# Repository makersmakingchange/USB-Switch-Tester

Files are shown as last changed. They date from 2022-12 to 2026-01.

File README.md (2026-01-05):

# USB SWITCH TESTER
The USB Switch Tester is used to test the functionality of an assistive switch with a 3.5 mm connection.

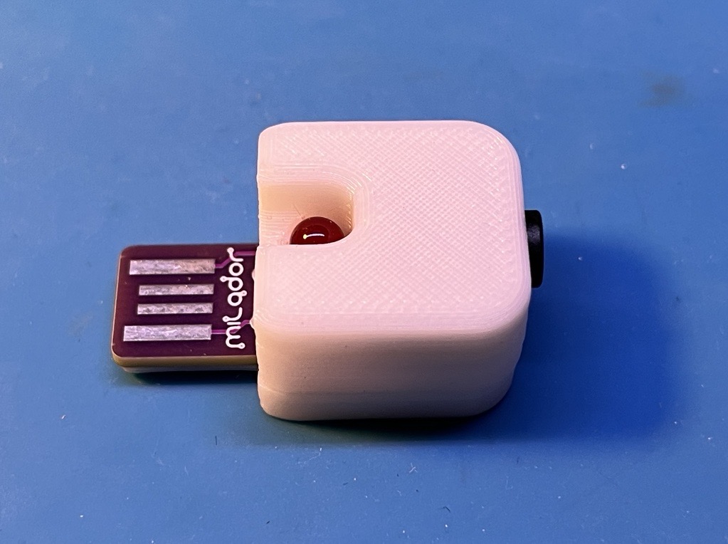
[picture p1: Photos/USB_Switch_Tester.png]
Picture of USB Switch Tester.


## More info at
- [Makers Making Change Assistive Device Library ](https://www.makersmakingchange.com/product/usb-switch-tester/01tJR000000690rYAA)

## How to Obtain a USB Switch Tester
### 1. Do it Yourself (DIY) or Do it Together (DIT)

This is an open-source assistive technology, so anyone is free to build it. All of the files and instructions required to build the USB Swtich Tester are contained within this repository. Refer to the Maker Checklist below.

### 2. Request a build of this device

If you would like to obtain a USB Switch Tester , you may submit a build request through the [MMC Library Page](https://www.makersmakingchange.com/product/usb-switch-tester/01tJR000000690rYAA). The requestor is responsible for the cost of materials and any shipping.

### 3. How to build this device for someone else

If you have the skills and equipment to build this device, and would like to donate your time to create the switch for someone who needs it, visit the [MMC Maker Wanted](https://makersmakingchange.com/maker-wanted/) section.

## Getting Started

### 1. Read the Makers Checklist

The Makers Checklist contains a list of tasks to complete to build the device.

### 2. Order the Off-The-Shelf Components

The [Bill of Materials](/Documentation/USB_Switch_Tester_BOM.xlsx) lists all of the parts and components required to build the USB Switch Tester. The main switch component needs to be ordered online. The rest of the off-the-shelf components are also online or may be available in smaller quantities at your local hardware store or dollar store.

### 3. Print the 3D Printable components

Print the top and bottom components of the case of the device. 

All of the files and individual print files can be in the [/Build_Files/3D_Printing_Files](/Build_Files/3D_Printing_Files/) folder.

### 4. Assemble the USB Switch Tester

Reference the [Assembly Guide](/Documentation/USB_Switch_Tester_Assembly_Guide.pdf) for the tools and steps required to build each portion.

## Files
### Documentation
| Document             | Version | Link |
|----------------------|---------|------|
| Design Rationale     | 1.0     | [USB_Switch_Tester_Design_Rationale](/Documentation/USB_Switch_Tester_Design_Rationale.pdf)     |
| Maker Checklist      | 1.0     | [USB_Switch_Tester_Checklist](/Documentation/USB_Switch_Tester_Maker_Checklist.pdf)     |
| Bill of Materials    | 1.0     | [USB_Switch_Tester_Bill_of_Materials](/Documentation/USB_Switch_Tester_BOM.xlsx)     |
| 3D Printing Guide    | 1.0     | [USB_Switch_Tester_3D_Printing_Guide](/Documentation/USB_Switch_Tester_3D_Printing_Guide.pdf)     |
| Assembly Guide       | 1.0     | [USB_Switch_Tester_Assembly_Guide](/Documentation/USB_Switch_Tester_Assembly_Guide.pdf)     |
| User Guide           | 1.0     | [USB_Switch_Tester_User_Guide](/Documentation/USB_Switch_Tester_User_Guide.pdf)    |
| Changelog            | 1.0     | [USB_Switch_Tester_Changelog](/Documentation/USB_Switch_Tester_Changelog.pdf)     |

### Design Files
 - [CAD Files](/Design_Files/CAD)
 - [PCB Design Files](/Design_Files/PCB)

### Build Files
 - [3D Printing Files](/Build_Files/3D_Printing_Files)
 - [PCB Gerber Files](/Build_Files/PCB_Files)

## Attribution
Designers:
 - Milad Hajihassan
 - Derrick Andrews

## License
Everything needed or used to design, make, test, or prepare the USB Switch Tester is licensed under the CERN 2.0 Weakly Reciprocal license <https://ohwr.org/project/cernohl/wikis/Documents/CERN-OHL-version-2> (CERN-OHL-W) . 

Accompanying material such as instruction manuals, videos, and other copyrightable works that are useful but not necessary to design, make, test, or prepare the USB Switch Tester are published under a Creative Commons Attribution-ShareAlike 4.0 license https://creativecommons.org/licenses/by-sa/4.0/ (CC BY-SA 4.0).

---
<!-- ABOUT MMC START -->

## About Makers Making Change
[Makers Making Change Logo](https://www.makersmakingchange.com/)

Makers Making Change is a program of [Neil Squire](https://www.neilsquire.ca/), a Canadian non-profit that uses technology, knowledge, and passion to empower people with disabilities.

Makers Making Change leverages the capacity of community based Makers, Disability Professionals and Volunteers to develop and deliver affordable Open Source Assistive Technologies.

 - Website: [www.MakersMakingChange.com](https://www.makersmakingchange.com/)
 - GitHub: [makersmakingchange](https://github.com/makersmakingchange)
 - Bluesky: [@makersmakingchange.bsky.social](https://bsky.app/profile/makersmakingchange.bsky.social)
 - Instagram: [@makersmakingchange](https://www.instagram.com/makersmakingchange)
 - Facebook: [makersmakechange](https://www.facebook.com/makersmakechange)
 - LinkedIn: [Neil Squire Society](https://www.linkedin.com/company/neil-squire-society/)
 - Thingiverse: [makersmakingchange](https://www.thingiverse.com/makersmakingchange/about)
 - Printables: [MakersMakingChange](https://www.printables.com/@MakersMakingChange)

### Contact Us
For technical questions, to get involved, or to share your experience we encourage you to [visit our website](https://www.makersmakingchange.com/) or [contact us](https://www.makersmakingchange.com/s/contact).
<!-- ABOUT MMC END -->

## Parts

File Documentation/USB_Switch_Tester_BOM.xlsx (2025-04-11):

USB Switch Tester |  |  |  |  |  |  |  | Unit Cost | Total Cost | Total Print time (hr) | Total filament (g)
Version: V1.0 |  | Last Updated: 2022-11-21 |  |  |  |  |  | $7.74 | $30.05 | 0.45 | 3.78
Commercial Parts
ID | Part Name | Part Type | QTY | QTY/PKG | $/PKG | PKG QTY | $/Unit | Extended | Total | Link
 | Led, 5 MM, Red | Electrical | 1 | 1 | $0.66 | 1 | $0.66 | $0.66 | $0.66 | https://www.mouser.ca/ProductDetail/604-WP7113ID5V
 | Resistor, 1 kOhms, 1/4W, Through Hole | Electrical | 1 | 1 | $0.24 | 1 | $0.24 | $0.24 | $0.24 | https://www.mouser.ca/ProductDetail/KOA-Speer/CFS1-4C102J?qs=9IB2bDhijq9MRkvwLBYZPw%3D%3D
 | Jack, 3.5 mm, Stereo, STX-3120-3B | Electrical | 1 | 1 | $1.15 | 1 | $1.15 | $1.15 | $1.15 | https://www.mouser.ca/ProductDetail/806-STX-3120-3B
3D Printed Parts ESTIMATED PRICING USING 1KG ROLL COST: |  | $25.00
ID | Part | Material | QTY | Mass (g) / Unit | Time / Unit Min |  | Print Time (Min) | Estimated Price |  | Link
 | Bottom | PLA ( 20% Infill ) | 1 | 1.49 | 10 |  | 10 | $0.04
 | Top | PLA (20% Infill ) | 1 | 2.29 | 17 |  | 17 | $0.06
 |  |  |  |  |  |  |  | $0.00
Custom Printed Circuit Board (PCB)
ID | Part |  | QTY
 | USB_Switch_Tester.zip |  | 1 | 5 | $28.00 | 1 | $5.60 | $5.60 | $28.00 | Build_Files/PCB_Files/Gerber_Files/USB_Switch_Tester.zip
Tools for Assembly
Soldering iron
flush cutters
Alternatives (if there are other sources for some parts link them below)
ID | Part and description |  |  |  |  |  |  |  |  | Link

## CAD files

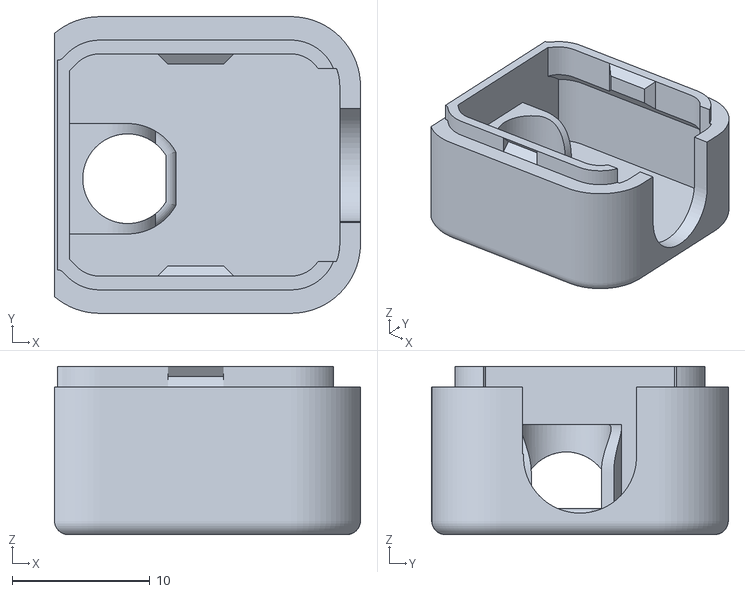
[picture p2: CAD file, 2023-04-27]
Build_Files/3D_Printing_Files/USB_Switch_Tester_Top_Case.stl
22.2 x 21.5 x 12.2

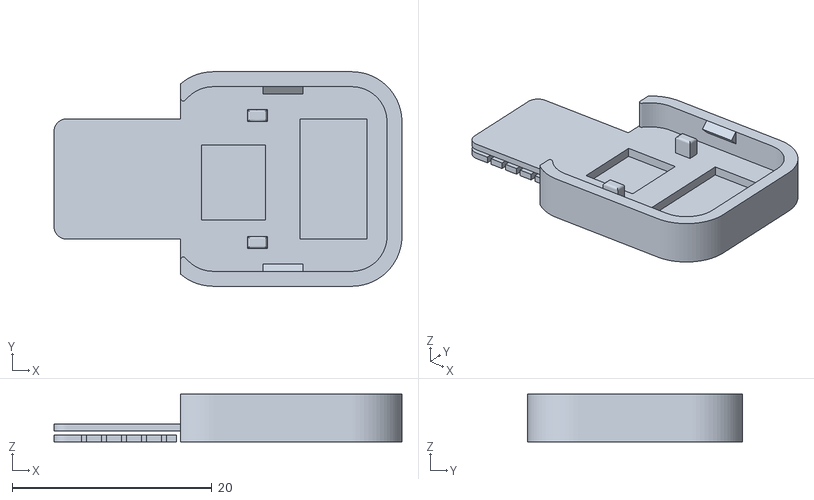
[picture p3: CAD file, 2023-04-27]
Build_Files/3D_Printing_Files/USB_Switch_Tester_Bottom_Case.stl
34.9 x 21.5 x 4.80

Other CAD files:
Design_Files/CAD/STEP/USB_Switch_Tester_Top_Case.step
Design_Files/CAD/STEP/USB_Switch_Tester_Bottom_Case.step
Design_Files/CAD/Fusion/USB_Switch_Tester.f3d
Design_Files/CAD/Fusion/USB_Switch_Tester_Complete.f3z

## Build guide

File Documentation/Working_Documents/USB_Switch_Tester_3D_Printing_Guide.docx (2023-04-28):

# 3D Printing Summary

Metrics
Total Print Time (min) | 30
Total Number of Components | 2
Typical Total Mass (g) | 3.76
Typical Number of Print Setups | 1

# 3D Printing Settings

Print File Name | Qty | Total Print Time (hr:min) | Mass (g) | Infill (%) | Support(Y/N) | Layer Height/ Nozzle Diameter(mm) | Notes (orientation, special settings, etc.)
Bottom_Case.stl | 1 | 0:12 | 1.56 | 20 | N | 0.2/0.4 | Print in default orientation shown below.
Top_Case.stl | 1 | 0:18 | 2.20 | 20 | N | 0.2/0.4 | Print in default orientation shown below.

## Default Orientation

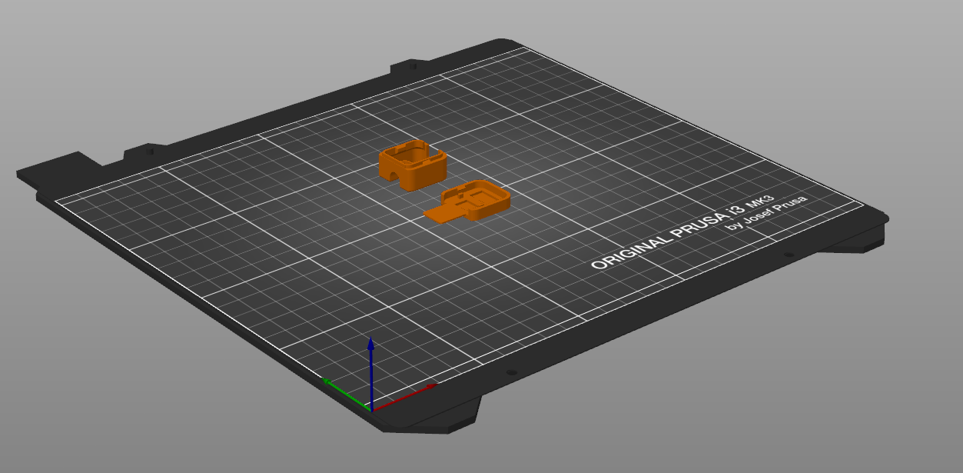
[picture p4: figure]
Photo of the top and bottom case inside of the Prusa Slicer software in default orientation.

# Examples of Quality Prints

The below photos are examples of the 3D printed components that are determined to meet the quality necessary for the device to function.

Photos of Top Case

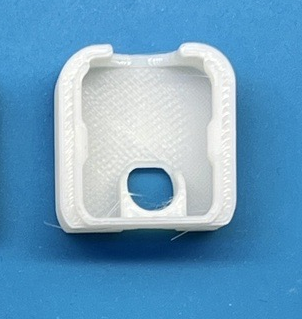
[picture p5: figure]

Photos of Bottom Case

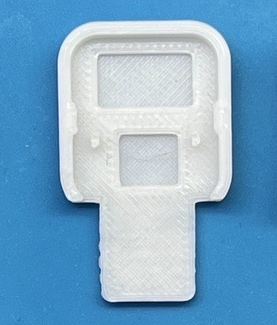
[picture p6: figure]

Photos of Assembly

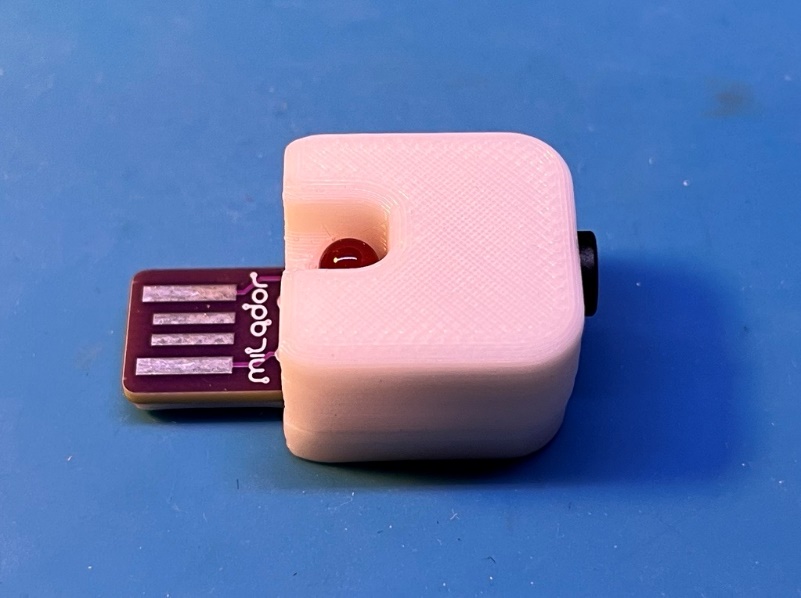
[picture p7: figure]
Photo of assembled top and bottom case with good quality print

© 2022 by Neil Squire / Makers Making Change. This work is licensed under the CC BY SA 4.0 License: http://creativecommons.org/licenses/by-sa/4.0 Files available at https://makersmakingchange.com/project/usb-switch-tester/ Page 1 of 2

V1.0 | April 2023 USB-Switch-Tester 3D Printing Guide

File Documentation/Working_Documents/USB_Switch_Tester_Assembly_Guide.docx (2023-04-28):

# Required Components

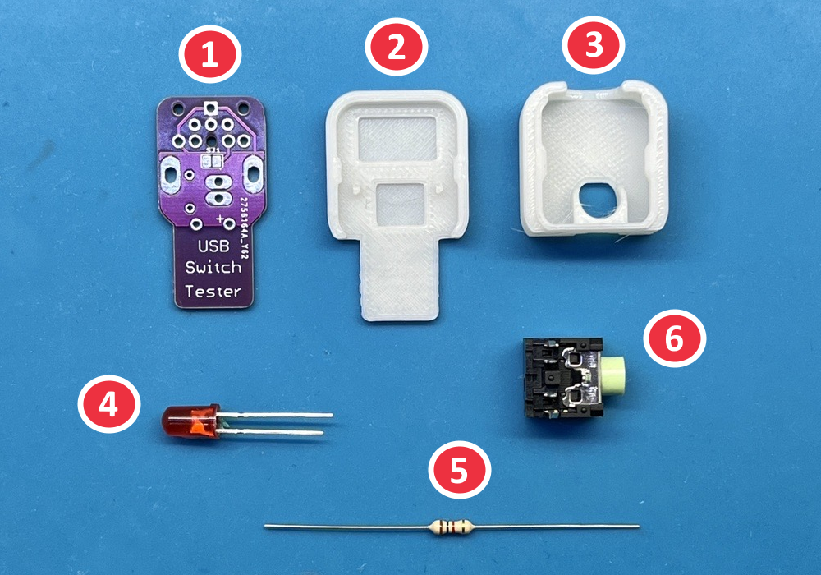
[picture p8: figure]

BOM

1. 1X USB-Switch-Tester PCB (Printed Circuit Board)
2. 1X USB-Switch-Tester Bottom Case
3. 1X USB-Switch-Tester Top Case
4. 1X 5MM Red LED
5. 1X 1KOhm Through-Hole Resistor
6. 1X STX-3120-5B 3.5mm Jack Stereo

# Required Tools

- Temperature regulated soldering Iron
- Phillips Screwdriver
- Side cutters

# Required Personal Protective Equipment (PPE)

- Safety glasses
- Disposable examination gloves (Optional- solder residue may irritate sensitive skin)

# Assembly Instructions

PCB Sides:

In these instructions the terms component side and solder side are used often and are defined below:

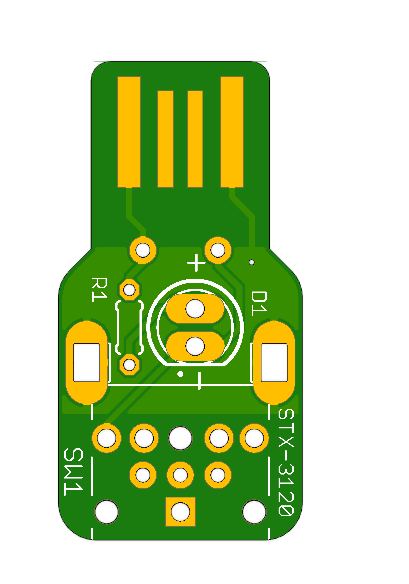
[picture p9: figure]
Component side CAD model of PCB.
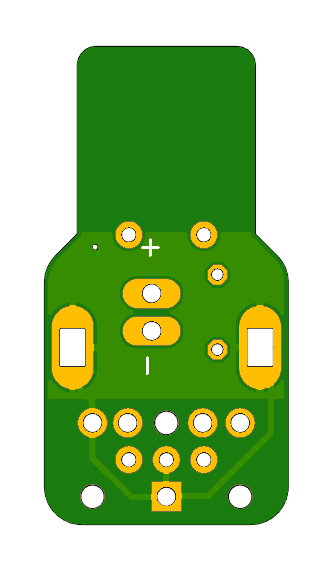
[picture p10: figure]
Solder side CAD model of PCB.

Component Side - USB metal rectangle contact points can be seen. - Visible painted white lines can be seen on this side of the board outlining a circle, R1, and D1. - The side of the PCB board with the label “Milador” is the component side of the PCB (not pictured in above photo). | Solder Side - No USB metal rectangle contact points can be seen - The side of the PCB board with the label “USB Switch Tester” is the component side of the PCB (not pictured in above photo).

## Step 1

Insert the LED into component side of the PCB (shown). Make sure the longer lead of the LED (positive lead) goes into the side marked “+” (closest to USB edge connector). Also ensure the LED is all the way in, and flush with the PCB.

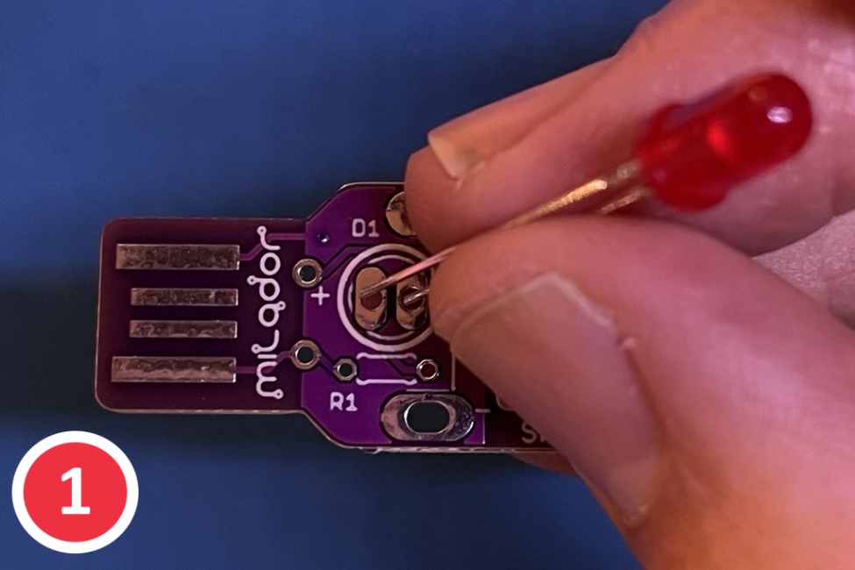
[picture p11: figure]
Component side of PCB facing up with a hand placing in a red LED

## Step 2

Using the heated soldering iron, solder the two LED terminals on the solder side of the PCB.

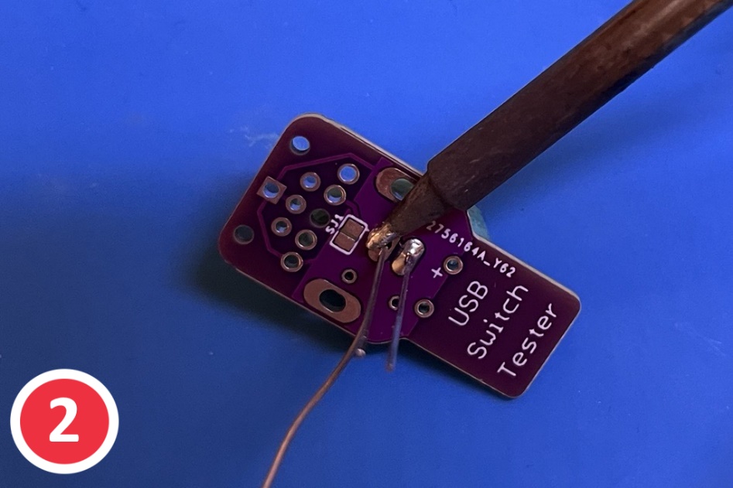
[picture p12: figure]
Soldering the red LED in on the solder side of the PCB

## Step 3

Using side cutters, trim the LED leads from the freshly soldered joints, as close to the board as possible.

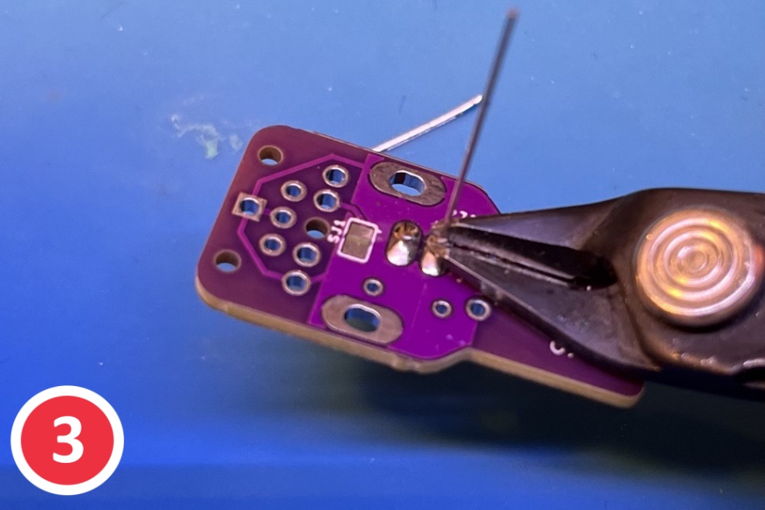
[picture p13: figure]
flush cutters cutting the extra length of the LED leads on the solder side of the PCB

## Step 4

Bend both leads of the 1K resistor (marked with stripes: brown black red) to 90 degrees next to the resistor body. After bending, both resistor leads should be parallel, and pointing in the same direction.

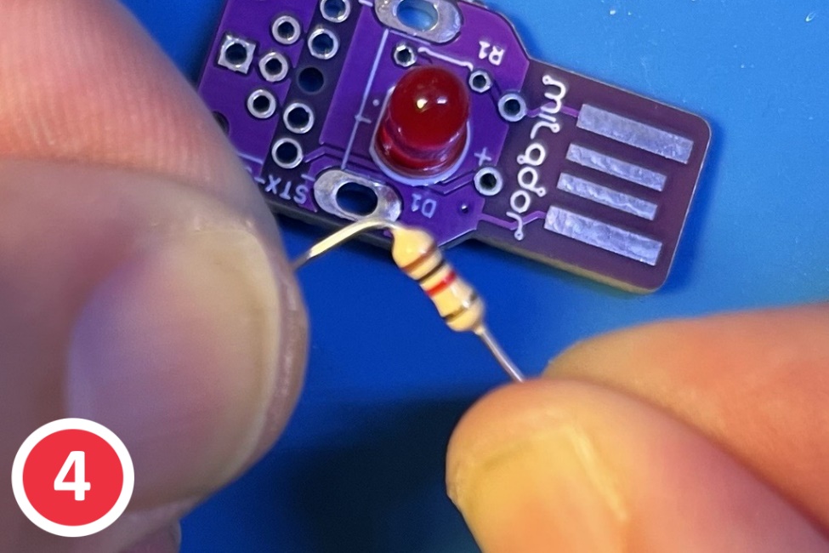
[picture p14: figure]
A hand bending the leads of the resister at 90 degrees

## Step 5

Insert the resistor into the resistor outline R1 holes next to the LED, as shown.

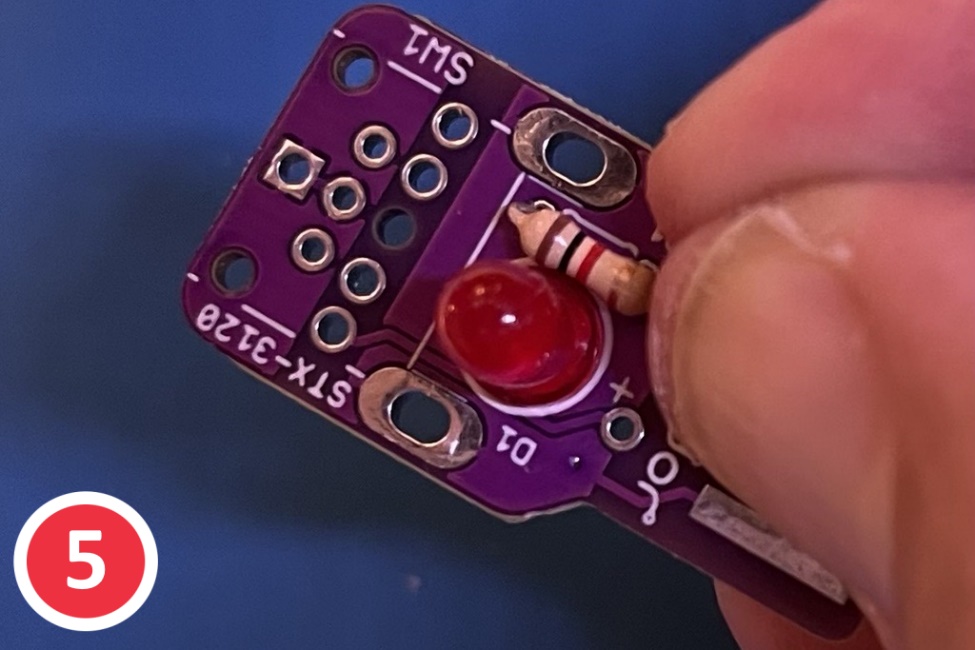
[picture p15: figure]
A hand placing the resistor into the PCB

## Step 6

Ensure the resistor is flush with board, then bend the resistor wires apart slightly, to minimize unwanted part movement during soldering.

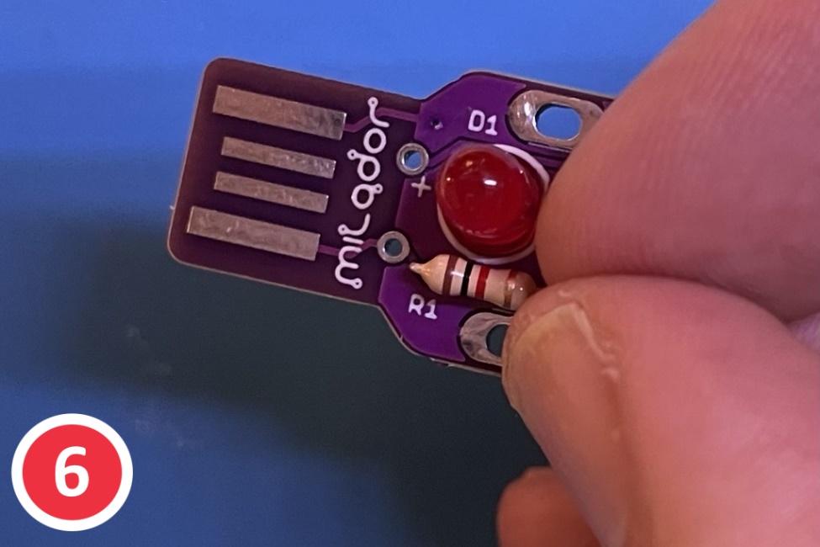
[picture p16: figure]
A finger holding the resistor close to the PCB

## Step 7

Using the heated soldering iron, solder the resistor wires on the solder side of the PCB.

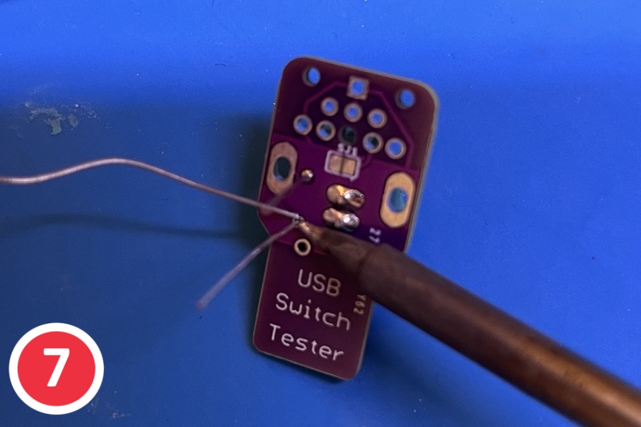
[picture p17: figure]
Soldering the leads of the resistor

## Step 8

Using side cutters, trim the resistor leads from the freshly soldered joints, as close to the board as possible.

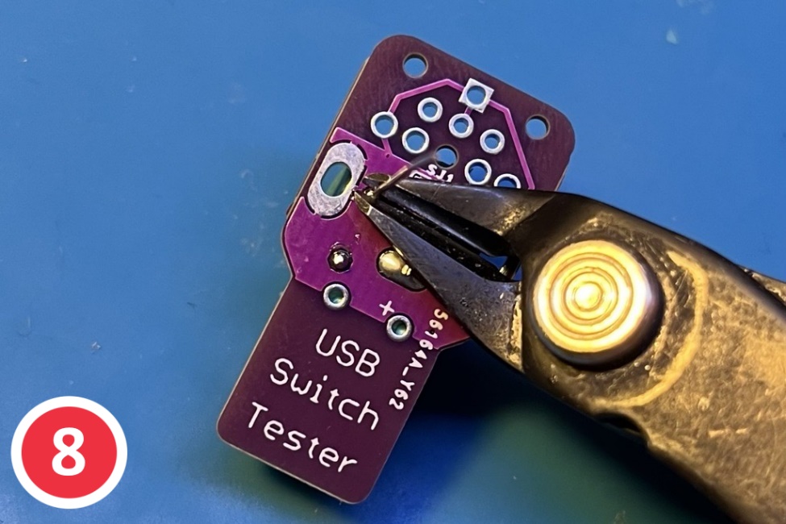
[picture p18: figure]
Using flush cutters to cut the extra of the resistor leads

## Step 9

Insert the 3.5 mm jack pins into the holes on the contact side of the PCB with the jack hole facing away from the LED.

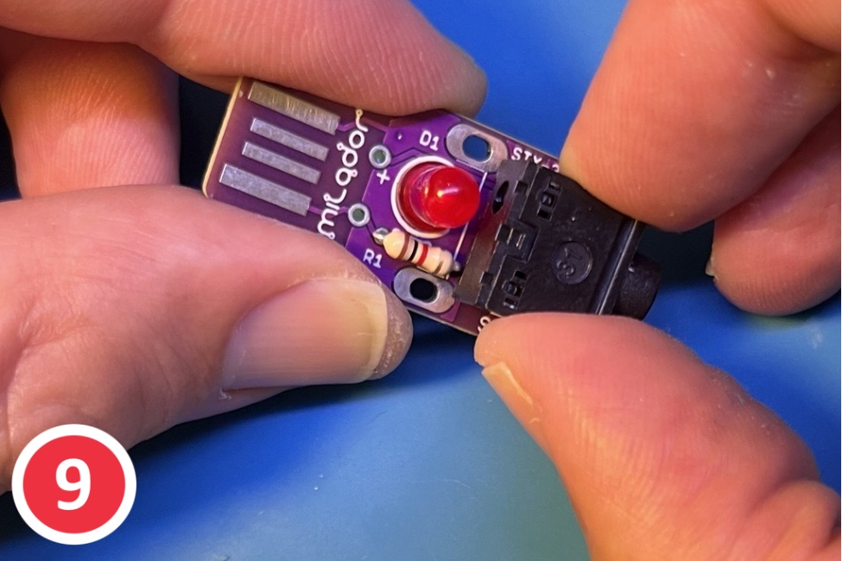
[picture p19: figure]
A hand placing the jack onto the PCB
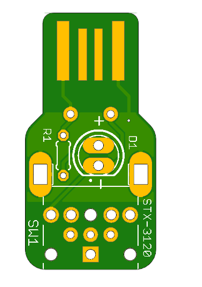
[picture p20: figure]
Photo of CAD model of PCB with a red arrow pointing to the holes the jack will fit into

## Step 10

Using the heated soldering iron, solder the 3.5 mm jack pins on the solder side of the PCB.

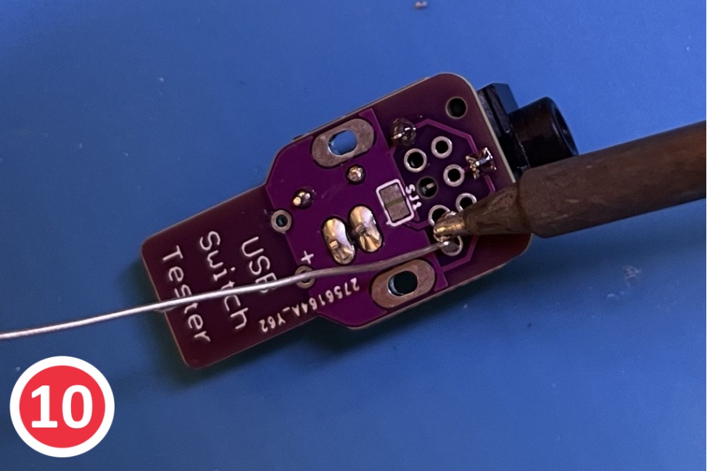
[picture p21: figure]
Soldering the leads of the jack

## Step 11

Using side cutters, trim the 3.5 mm jack leads from the freshly soldered joints, as close to the board as possible.

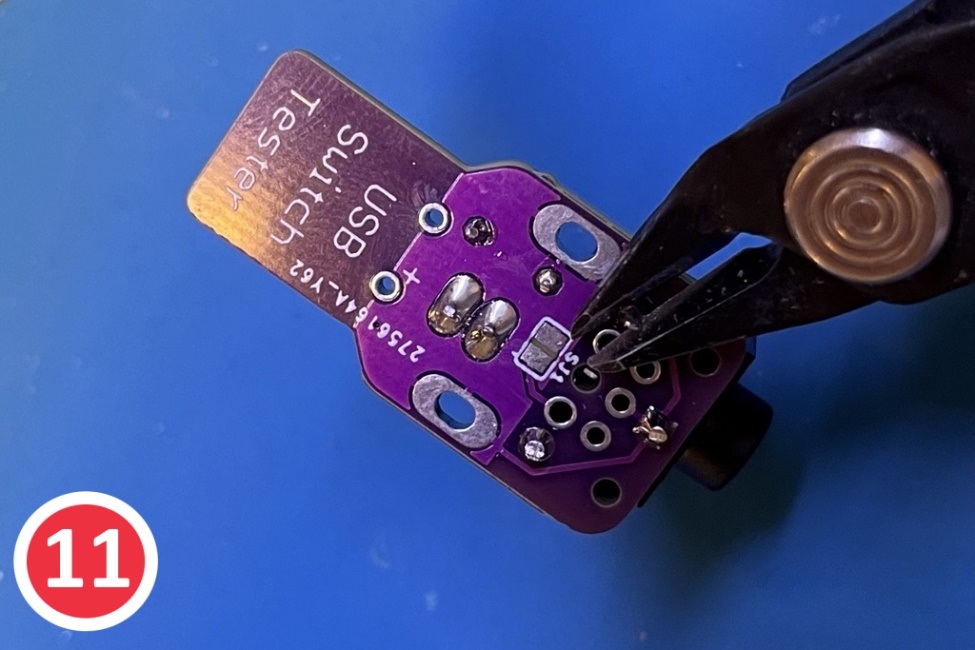
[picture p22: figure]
using flush cutters to cut the extra on the leads of the jack

## Step 12 – Preliminary Testing

All electronic components are now assembled and the device can be tested. To test follow the steps below:

1. Plug in the PCB into a USB port that has power. An example of this would be to plug the USB into a USB Type A port on a laptop.
2. Plug in an adaptive switch with a 3.5 mm plug into the 3.5 mm jack.
3. Press down on the adaptive switch
4. If the light:
  a. Turns on when you press the adaptive switch the test was successful and move on to Step 13.
  b. Does not turn on check the solder connections on the solder side of the device and make sure there is no connections touching.

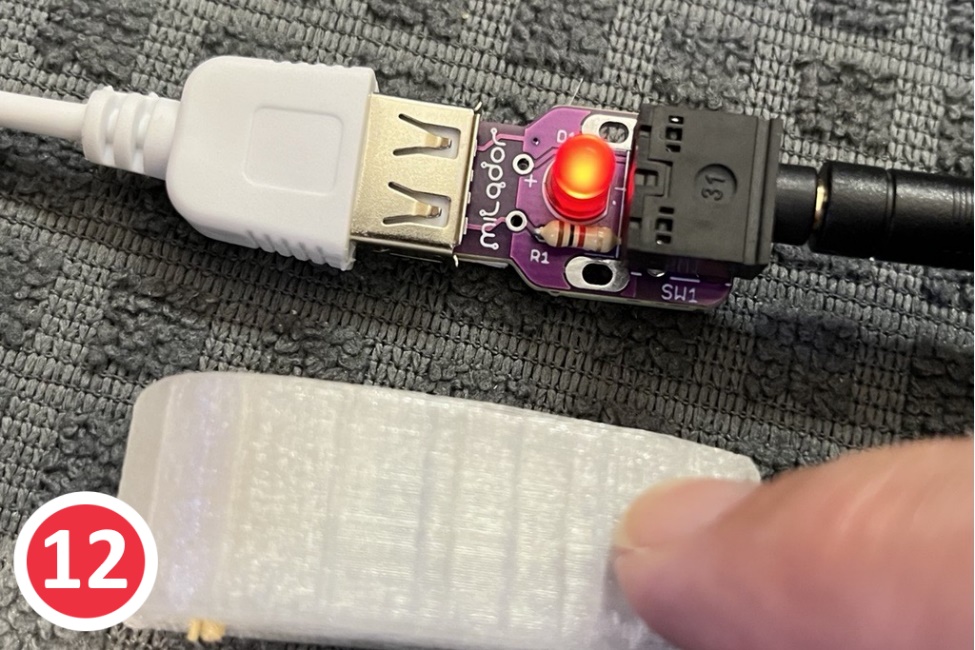
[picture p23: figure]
Photo of the USB switch tester plugged into a USB port and a finger pressing an assistive switch that is plugged into he USB Switch Tester. The red LED light is turned on.

## Step 13

Insert the electronic assembly into the 3D printed top case. Locate the cut outs on the top case for the 3.5 mm jack and LED. Ensure the jack and LED fit inside of these exits.

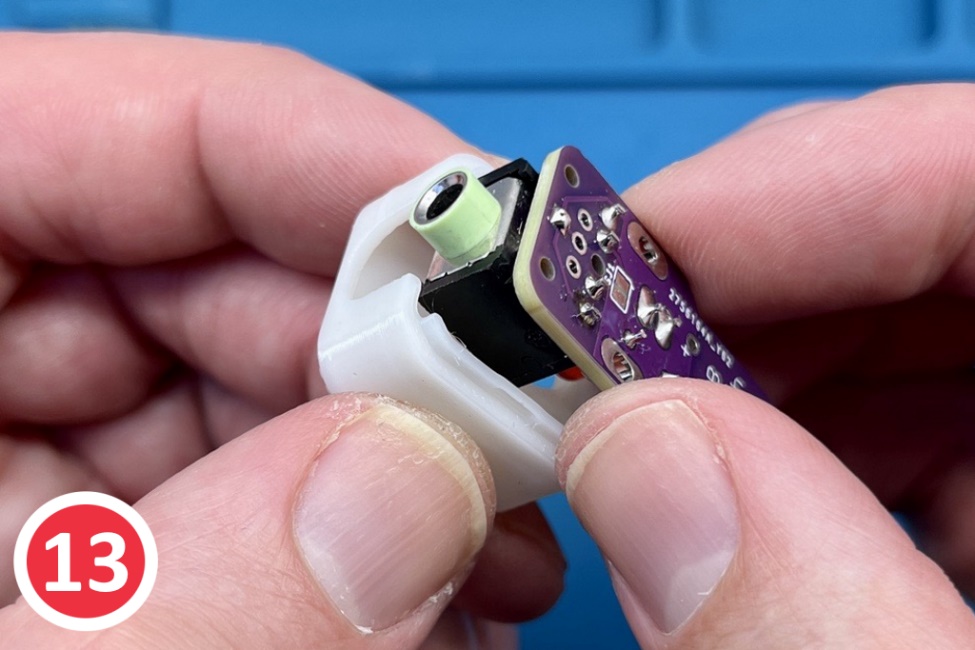
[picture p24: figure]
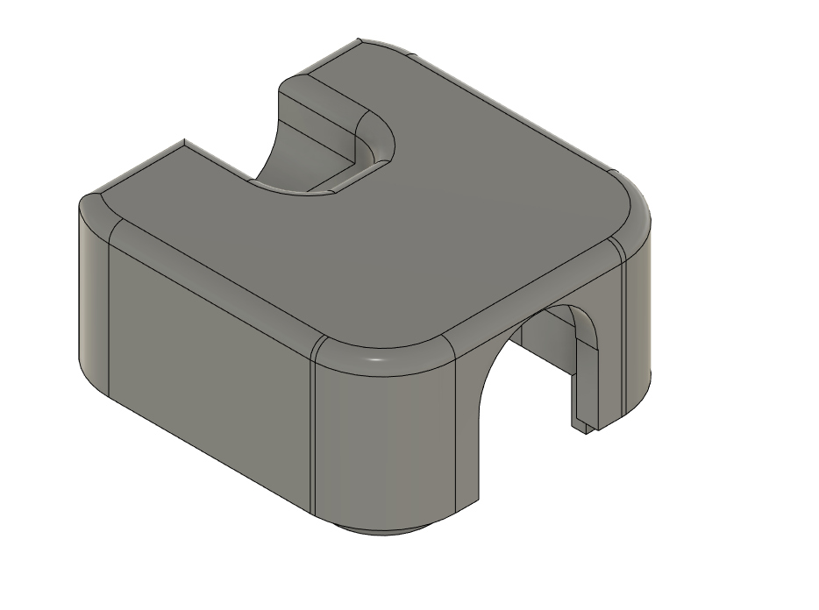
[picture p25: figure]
A photo with a red arrow pointing to the jack exit
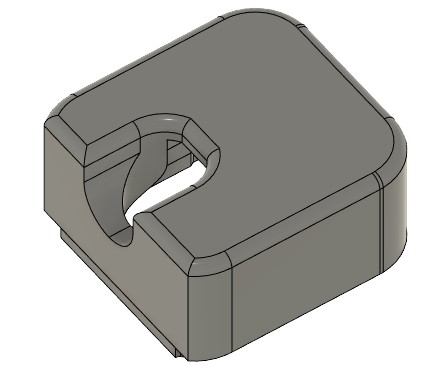
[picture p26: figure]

| 3.5 mm Jack exit LED exit

## Step 14

Place the 3D printed bottom case on the solder side of the PCB and press down gently until you feel the top and bottom case clip together. After the top and bottom case are clipped together the whole device should feel secured.

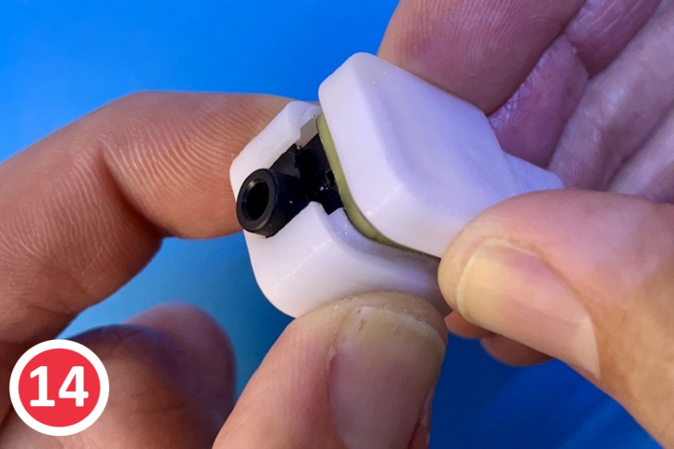
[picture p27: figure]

## Step 15

The assembly is complete, congratulations! Please refer to the Maker Checklist document that can be found on the website page for this device for the next steps.

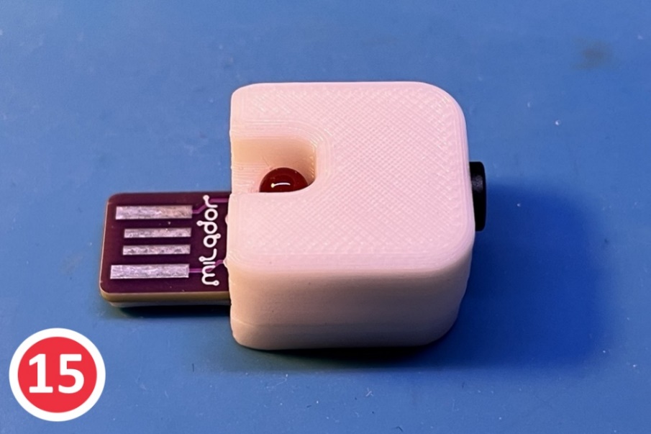
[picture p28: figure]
A photo of the assembled USB Switch Tester device

© 2022 by Neil Squire / Makers Making Change. This work is licensed under the CC BY SA 4.0 License: http://creativecommons.org/licenses/by-sa/4.0 Files available at https://makersmakingchange.com/project/usb-switch-tester/ Page 1 of 1

V1.0 | April 2023 USB-Switch-Tester Assembly Guide

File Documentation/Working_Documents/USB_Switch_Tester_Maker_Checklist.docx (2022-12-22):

# Maker To Do List

- Read through the Assembly Guide to become familiar with required components, tools, supplies, and safety gear and overall assembly steps.
- Talk to User about customization options (e.g., color, any special requests, etc.)
- Order hardware components
- Gather tools, supplies, and safety equipment.
- Assemble the device
- Test device
- Print “User Quick Guide”

# Items to Give to User

- Assembled, tested device
- “User Quick Guide”

© 2022 by Neil Squire / Makers Making Change. This work is licensed under the CC BY SA 4.0 License: http://creativecommons.org/licenses/by-sa/4.0 Files available at https://makersmakingchange.com/project/usb-switch-tester/ Page 1 of 1

V1.0 | December 2022 USB-Switch-Tester Maker Checklist

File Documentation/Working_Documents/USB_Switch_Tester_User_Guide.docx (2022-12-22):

## Introduction

This USB Switch Tester is a device that allows someone to confirm their assistive switch with a 3.5 mm plug is functional. This convenient device can be plugged into USB Type-A ports with power (for example, a laptop) and assistive switches can be plugged in to the 3.5 mm jack on the USB switch tester. When the assistive switch is pressed down, the LED on the device will light up indicating that the assistive switch is working. If the assistive switch is not working, the LED on the USB Switch Tester will not light up. This device will be helpful to disability professionals or individuals who use assistive switches to check to make sure their devices are in working condition.

This is NOT a switch interface but rather a simple device to confirm your assistive switch is working properly.

## Features

The USB Switch Tester features an LED light, USB plug, 3D printed casing, and a 3.5 mm port as shown in the photo below.

LED light – Lights up when a working assistive switch is pressed.

3.5 mm port – Location where assistive switches with a 3.5 mm plug will be inserted.

USB plug – Allows device to be inserted into a powered USB port.

3D printed casing – hard outer shell that protects the internal electrical components.

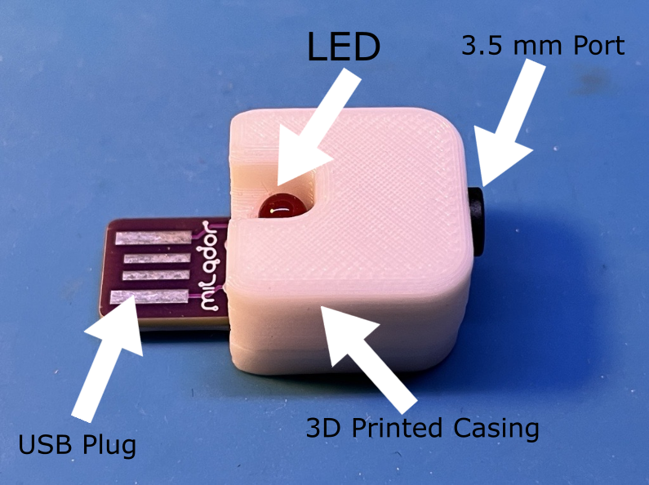
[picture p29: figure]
A photo of the assembled USB Switch testers with white arrows pointing to the LED, 3.5 mm port, 3D printed casing, and USB plug

## Usage

This device requires a USB port that has power coming from it and an assistive switch to test. The setup should look similar to the one shown in the photo below. With these materials, follow the below steps:

1. Plug the USB Switch Tester into the powered USB port (see compatibility section to see powered USB ports).
2. Plug in the assistive switch that you would like to test
3. Press down on the assistive switch
  a. If the LED on the USB Switch Tester lights up, the assistive switch is functional
  b. If the LED on the USB Switch Tester does not light up, the assistive switch is not working
4. Unplug the assistive switch from USB Switch Tester and repeat steps above if you want to test another assistive switch

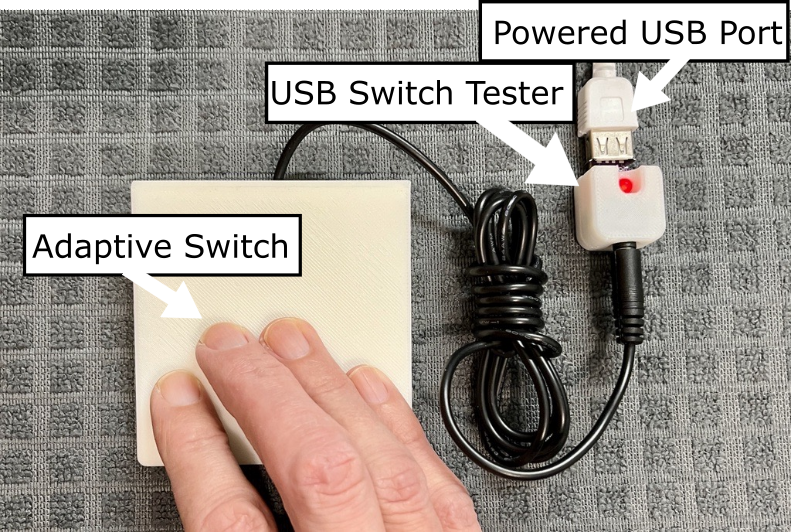
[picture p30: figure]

## Compatibility

This device needs to be plugged into a powered USB source. There are many options for this as the device does not draw more than 20 mA of current from the power source. The USB Switch Tester can be plugged into any power source with USB Type-A port such as laptops, USB block chargers, etc.

In the example photo below, the USB Switch Tester is plugged into a USB block charger that is connected to an outlet.

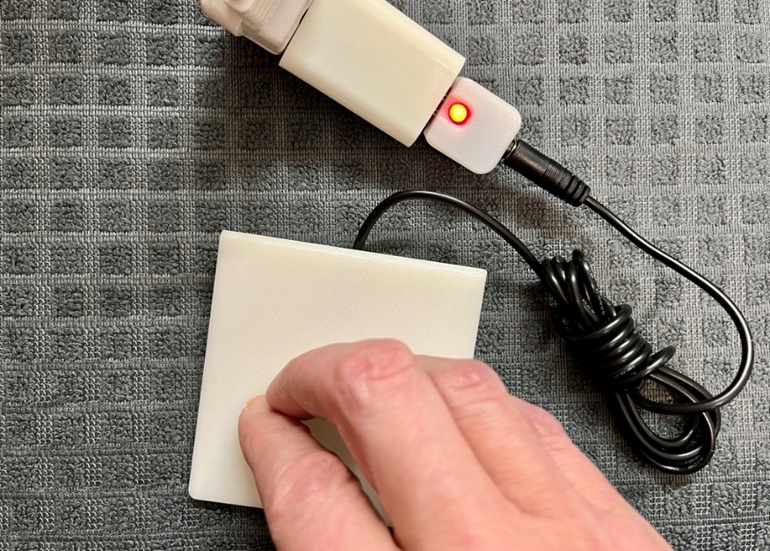
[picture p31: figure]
Tester device being plugged into a powered USB port and adaptive switch plugged into the tester. The adaptive switch is being pressed down with the red LED being lit up. The powered USB port is a block charger plugged into an outlet

## Specifications

Dimensions (mm) | | | Mass (g)
Length | Width | Height
33 | 17 | 13 | 7

## Cleaning

The USB Switch Tester can be wiped down with sanitizing cleaners or gently scrubbed with a soft-bristled brush. Do not subject the device to high heat as this may damage the 3D-printed material.

© 2022 by Neil Squire / Makers Making Change. This work is licensed under the CC BY SA 4.0 License: http://creativecommons.org/licenses/by-sa/4.0 Files available at https://makersmakingchange.com/project/rocket-switch-interface/ Page 2 of 3

V1.0 | December 2022 USB Switch Tester user Quick Guide

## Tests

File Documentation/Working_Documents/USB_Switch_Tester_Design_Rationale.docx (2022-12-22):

# Introduction

The USB Switch Tester is a device used to test the functionality of an assistive switch with a 3.5 mm connection. This device allows users to determine if they successfully assembled their switch adapted device and make sure that all the components are working. The existing switch tester device such as Simple Switch Tester require a power source which adds to the cost over time.

The USB Switch Tester is intended to use the existing USB power sources or USB power adapters which are very common as the power source. USB power adapters are available in most households and can be purchased locally.

This device is intended to be used by users of assistive switches or disability professionals to confirm the assistive switch is functional.

# Research

Existing Commercial Options

Title | Single Switch Tester
Link | https://www.ablenetinc.com/technology/single-switch-tester
Author | AbleNet
License
Cost | $55 USD
Notes | Discontinued?

DIY designs

Title | Simple Switch Tester
Link | https://makersmakingchange.com/project/simple-switch-tester/
Author | MakersMakingChange
License | Attribution-ShareAlike 4.0 International
Cost | $11 - $25 CAD
Test Build (Y/N) | Y
Add to Library (Y/N) | n/a
Notes | Battery powered

# Requirements

## Goals

ID | Description
G01 | Cost Effective (Low cost comparing to alternative options)
G02 | Easy to use
G03 | Easy to assemble
G04 | Minimal size

## Functional Requirements

F01 | The device shall have one input channel.
F02 | The device shall have a visual feedback element via a LED to notify the user about the switch activations.
F03 | The device latency shall not exceed 50 milliseconds.
F04 | The device shall not consume more than 20 mA of current from the USB port.
F05 | The device shall have a USB Type A PCB connector.

## Non-functional Requirement

NF01 | Shall look professional with tight tolerance on case size.
NF02 | The device shall weigh less than 25 grams.

## Constraints

C01 | Shall be able to be built as a single unit for ≤ $30 CAD
C02 | Shall be easily manufacturable by a moderately skilled maker

# Conceptual Design

## Through hole

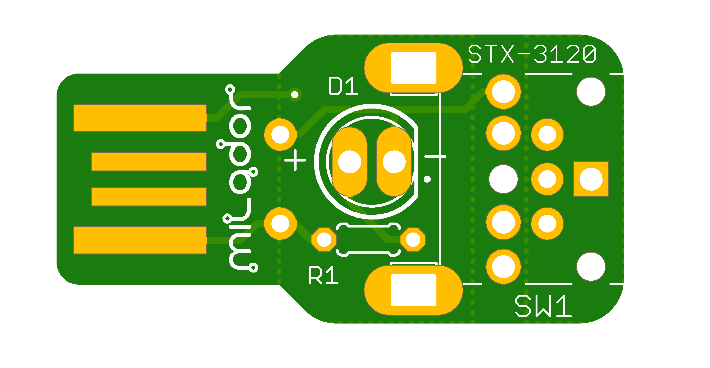
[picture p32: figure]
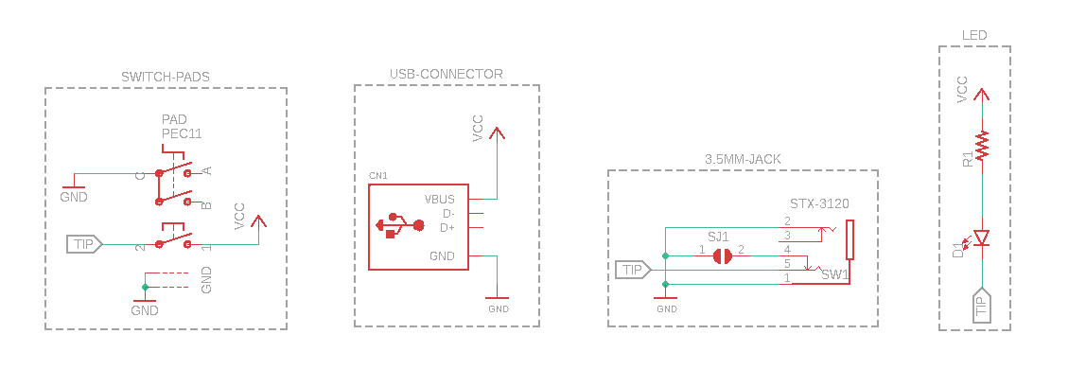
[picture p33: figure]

- Units: 5
- PCB Price: US $2.0
- Components: US $7.65 Or CAD $10.25
- Digikey shipping : US $6 or CAD $8
- Shipping :
  - Economical Global Direct Line
    - No tracking : US $3.70
    - 10-18 business days
    - Taxes will be levied at the check-out point for the order with an intrinsic value ≥15.5USD.Last mile service is provided by Canada Post.
  - Global Direct Line Saver
    - US $10.57
    - 8-15 business days
    - The last mile delivery service is provided by Canada Post.
- Total all : US $17.35 or CAD $23.25 or CAD $3.47 per unit

## SMT

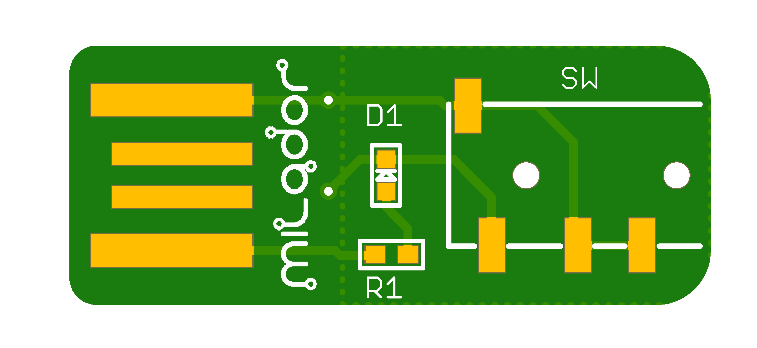
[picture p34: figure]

- Units: 5
- PCB Price: US $2.0
- SMT Price
  - Setup fee US $8.00
  - Stencil US $1.50
  - Panel US $0.00
  - Large Size US $0.00
  - Components US $0.72
  - Extended components fee
    - US $3.00
  - SMT Assembly
    - US $0.06
- Total Assembly and PCB: US $15.28
- Shipping :
  - Economical Global Direct Line
    - No tracking : US $3.70
    - 10-18 business days
    - Taxes will be levied at the check-out point for the order with an intrinsic value ≥15.5USD.Last mile service is provided by Canada Post.
  - Global Direct Line Saver
    - US $10.57
    - 8-15 business days
    - The last mile delivery service is provided by Canada Post.
- Total all : US $18.98 or CAD $25.5 or CAD $5.1 per unit

Concept | Through Hole | SMT
Units | 5 | 5
PCB Cost | US $2 | US $2
Total Assembly Cost | Volunteers time | US $15.28
Components Cost | US $7.65 | US $3.72
Components Shipping Cost | US $6 | None
Most affordable shipping Cost (Economical Global Direct Line) | US $3.70 | US $3.70
Total Cost | US $17.35 or CAD $23.25 | US $18.98 or CAD $25.5
Total Per Unit Cost | CAD $3.47 | CAD $5.1

© 2022 by Neil Squire / Makers Making Change. This work is licensed under the CC BY SA 4.0 License: http://creativecommons.org/licenses/by-sa/4.0 Files available at https://makersmakingchange.com/project/rocket-switch-interface/ Page 1 of 1

V1.0 | December 2022 USB-Switch-Tester Design Rationale

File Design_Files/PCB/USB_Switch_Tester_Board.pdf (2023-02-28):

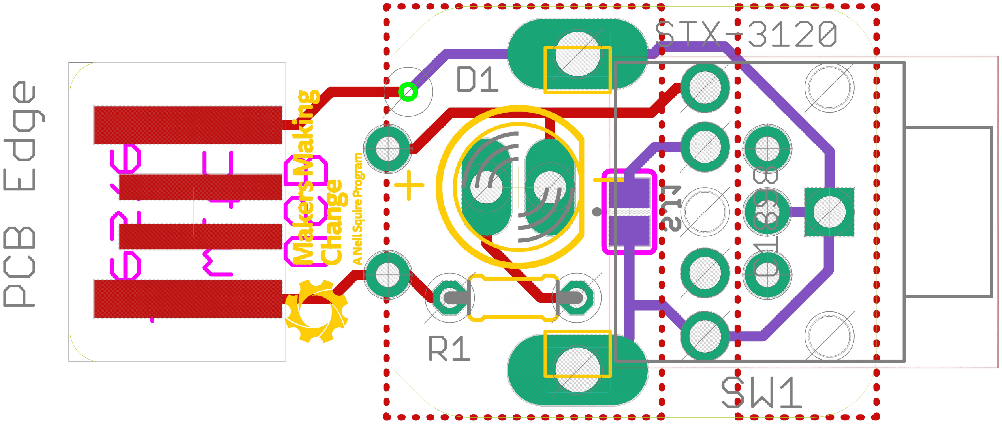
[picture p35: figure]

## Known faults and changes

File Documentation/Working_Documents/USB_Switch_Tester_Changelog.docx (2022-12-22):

# Version 1.0 | 2022/11/18

- Version created by Milad Hajihassan and Derrick Andrews.
- First version created with custom PCB design and 3D printed housing
- Full documentation package was created.
- All files shared on the Makers Making Change open source assistive technology library.

© 2022 by Neil Squire / Makers Making Change. This work is licensed under the CC BY SA 4.0 License: http://creativecommons.org/licenses/by-sa/4.0 Files available at https://makersmakingchange.com/project/usb-switch-tester/ Page 1 of 1

V1.0 | December 2022 USB Switch Tester changelog

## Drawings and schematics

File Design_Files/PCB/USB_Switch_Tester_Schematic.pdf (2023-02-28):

A

A

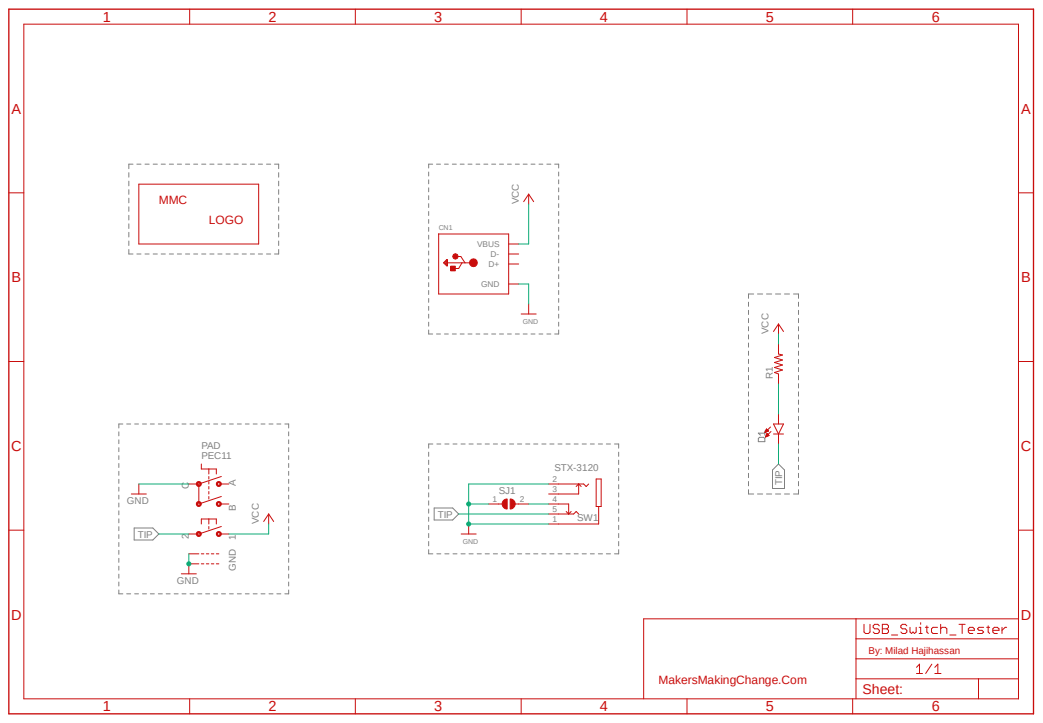
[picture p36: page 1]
GND; 1 A B C GND; PEC11; STX-3120 VCC VCC; VCC; D+D- GND; VBUS CN1 PAD; TIP; MMC; LOGO

By: Milad Hajihassan

MakersMakingChange.Com

Sheet:

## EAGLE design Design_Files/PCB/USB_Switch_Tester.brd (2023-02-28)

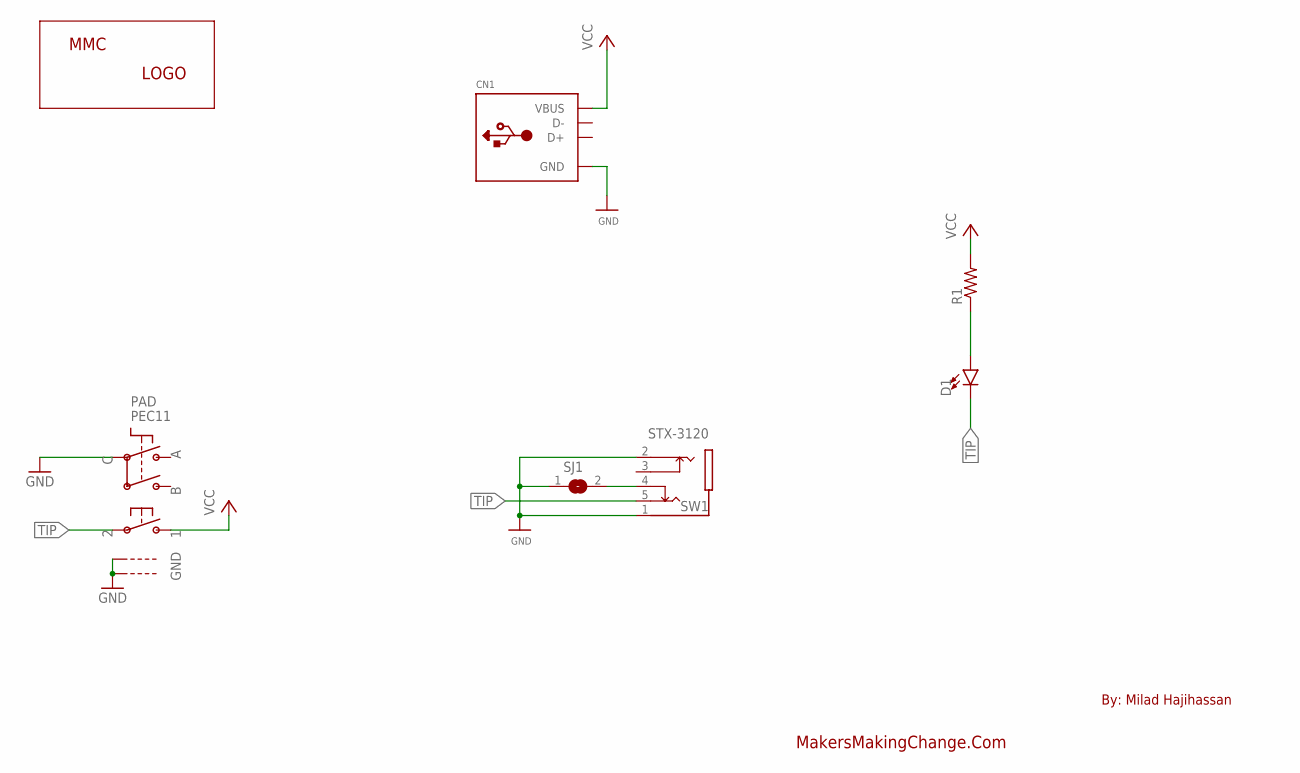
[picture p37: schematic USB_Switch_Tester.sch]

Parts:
CN1: MICROBUILDER_USB_TYPEAPCB; MICROBUILDER_USBA_PCB
D1: LED_5MM-5MM-RED; LED_5MM_RED
LABEL_LOGO: MMC_LOGO-XSM; MMC_X-SMALL_LOGO
PAD: PEC11; ADAFRUIT_ELECTROMECH_PEC11+SWITCH
R1: RESISTOR-US-0204/5; RESISTOR_0204/5
SJ1: SOLDERJUMPERREFLOW; SOLDERJUMPER_REFLOW
SW1: STX-3120; STX-3120-5B

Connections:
GND: CN1.GND, PAD.P$C, PAD.P$GND1, PAD.P$GND2, SJ1.1, SW1.1, SW1.2
unnamed: D1.A, R1.1
unnamed: SJ1.2, SW1.4
TIP: D1.K (C), PAD.P$2, SW1.5
VCC: CN1.VCC (VBUS), PAD.P$1, R1.2

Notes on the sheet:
By: Milad Hajihassan
MakersMakingChange.Com

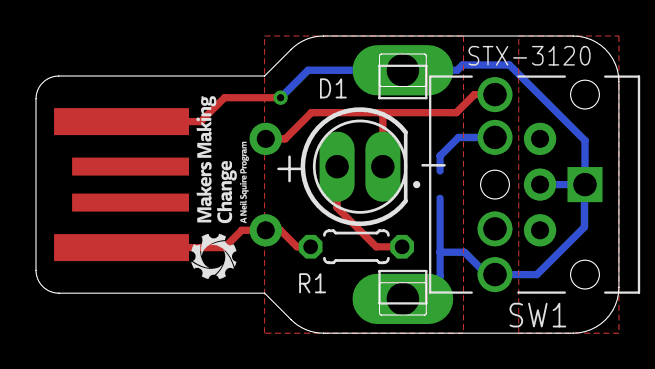
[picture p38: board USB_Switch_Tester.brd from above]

Board: 2 copper layers, 32.4 x 16.5 mm, 7 parts (1 on the bottom side), 5 nets.

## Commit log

2022-12-22 First upload of files
    [USB_Switch_Tester.brd, USB_Switch_Tester.f3d, USB_Switch_Tester.sch, USB_Switch_Tester_BOM.xlsx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]
2022-12-22 weird artifacts
    [USB_Switch_Tester_BOM.xlsx]
2023-02-28 Updated PCB: Added MMC Logo
    [USB_Switch_Tester.brd, USB_Switch_Tester.sch]
2023-04-27 Updated the enclosure design to simplify assembly process
    [USB_Switch_Tester.f3d, USB_Switch_Tester_Bottom_Case.step, USB_Switch_Tester_Bottom_Case.stl, USB_Switch_Tester_Complete.f3z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]
2023-04-28 Updated assembly guide
2025-04-11 Remove version from documentation file name
    [USB_Switch_Tester_BOM.xlsx, USB_Switch_Tester_BOM_v1.0.xlsx]
